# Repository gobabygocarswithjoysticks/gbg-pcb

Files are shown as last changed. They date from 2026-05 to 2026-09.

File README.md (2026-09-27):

# GBG PCB

# A PCB for controlling the motors in a [go baby go car with joystick control](https://gobabygocarswithjoysticks.github.io/index/)

## Questions? Please email our support line at gbg-pcb@googlegroups.com

https://github.com/gobabygocarswithjoysticks/gbg-pcb



V2.3

### This board replaces the control box of a car's original electronics or the separate ESCs and Arduino in the [usual joystick go baby go modification](https://gobabygocarswithjoysticks.github.io/index/). The board has screw terminals for connecting to the battery, motors, and the joystick. With this circuit board, a car can be converted to joystick control without any soldering.

### Voltage input: 6V, 12V, or 24V (absolute maximum 4.6V-35V)

### Controls two motors: one for each wheel so that the car can turn in place.

## V2 vs V1
* V2 GBG-PCBs (V2.3+) can run from 6-24 volt batteries.
* V2.1 and V2.2 GBG-PCBs can run from 6 to 12 volt batteries (maximum of 18 volts). 
* Version 1 GBG-PCBs had a higher, 10+ amp current capacity and a lower part count (easier assembly) but only runs on 12 volts.
* Version 2 boards can be [configured](https://gobabygocarswithjoysticks.github.io/gbg-pcb/instructions/instructions#new-in-v2-weelye-control-box-compatible) with battery, motor, and signal plugs that match the plugs on the common weelye control boxes. This means some cars can be converted to joystick control without cutting any wires. 
* Version 2 boards can supply [8 amps](/testing.md) per motor continuously.
* For the previous versions of the GBG-PCB see https://github.com/gobabygocarswithjoysticks/gbg-pcb/tree/version_1 

# Want one?
Here's a few options:
* Please feel free to use these [files](/PCB_production) and get boards yourself. There are instructions [here](https://gobabygocarswithjoysticks.github.io/gbg-pcb/instructions/how-to-make-boards/how-to-make-boards) for how to make GBG-PCBs by hand. A board costs approximately $40-$100 depending on what quantity it is built in.
* [Use this PCBWay link to order fully assembled boards](https://www.pcbway.com/project/shareproject/GBG_PCB_Go_Baby_Go_Printed_Circuit_Board_V2_2_standard_b412e472.html). Or, alternative PCBWay links if you want to complete the assembly yourself: [PCBWay can do everything but leave the battery, motor, and button connectors off](https://www.pcbway.com/project/shareproject/GBG_PCB_Go_Baby_Go_Printed_Circuit_Board_V2_2_no_motor_battery_or_button_c_74b587c3.html) or, [PCBWay can do the challenging surface mount soldering and leave the through-hole soldering for you](https://www.pcbway.com/project/shareproject/GBG_PCB_Go_Baby_Go_Printed_Circuit_Board_V2_2_SMD_only_f25d1936.html)
* Email gobabygocarswithjoysticks@gmail.com. We may have a spare V1 or V2 GBG-PCBs that I can sell or donate to you.
* Email pnwassistivetech@gmail.com or visit the [PNW Assistive Technology website](https://pnwassistivetechnology.org/plug-and-drive). Thank you to PNWAT for sponsoring V2 GBG-PCB prototyping runs and being a supplier of V1 and V2 GBG-PCBs (called "plug and drive boards" by PNWAT).

# Software
## The website for uploading software to a GBG-PCB and adjusting settings is here: https://gobabygocarswithjoysticks.github.io/programmer/

# Instructions
## [general instructions for using this PCB](https://gobabygocarswithjoysticks.github.io/gbg-pcb/instructions/instructions)
### [instructions for assembling your own GBG-PCBs](https://gobabygocarswithjoysticks.github.io/gbg-pcb/instructions/how-to-make-boards/how-to-make-boards)
## Index of Instructions for modifying specific models of cars using GBG-PCBs
* [Aosom Jeep - old model](https://gobabygocarswithjoysticks.github.io/gbg-pcb/instructions/car-specific/aosom-038-jeep/instructions)
* [Zupapa Bumper Car](https://gobabygocarswithjoysticks.github.io/gbg-pcb/instructions/car-specific/zupapa-bumper-car/instructions)
* [Flybar Bumper Car](https://gobabygocarswithjoysticks.github.io/gbg-pcb/instructions/car-specific/flybar-bumper-car/instructions)

# Wiring Diagram
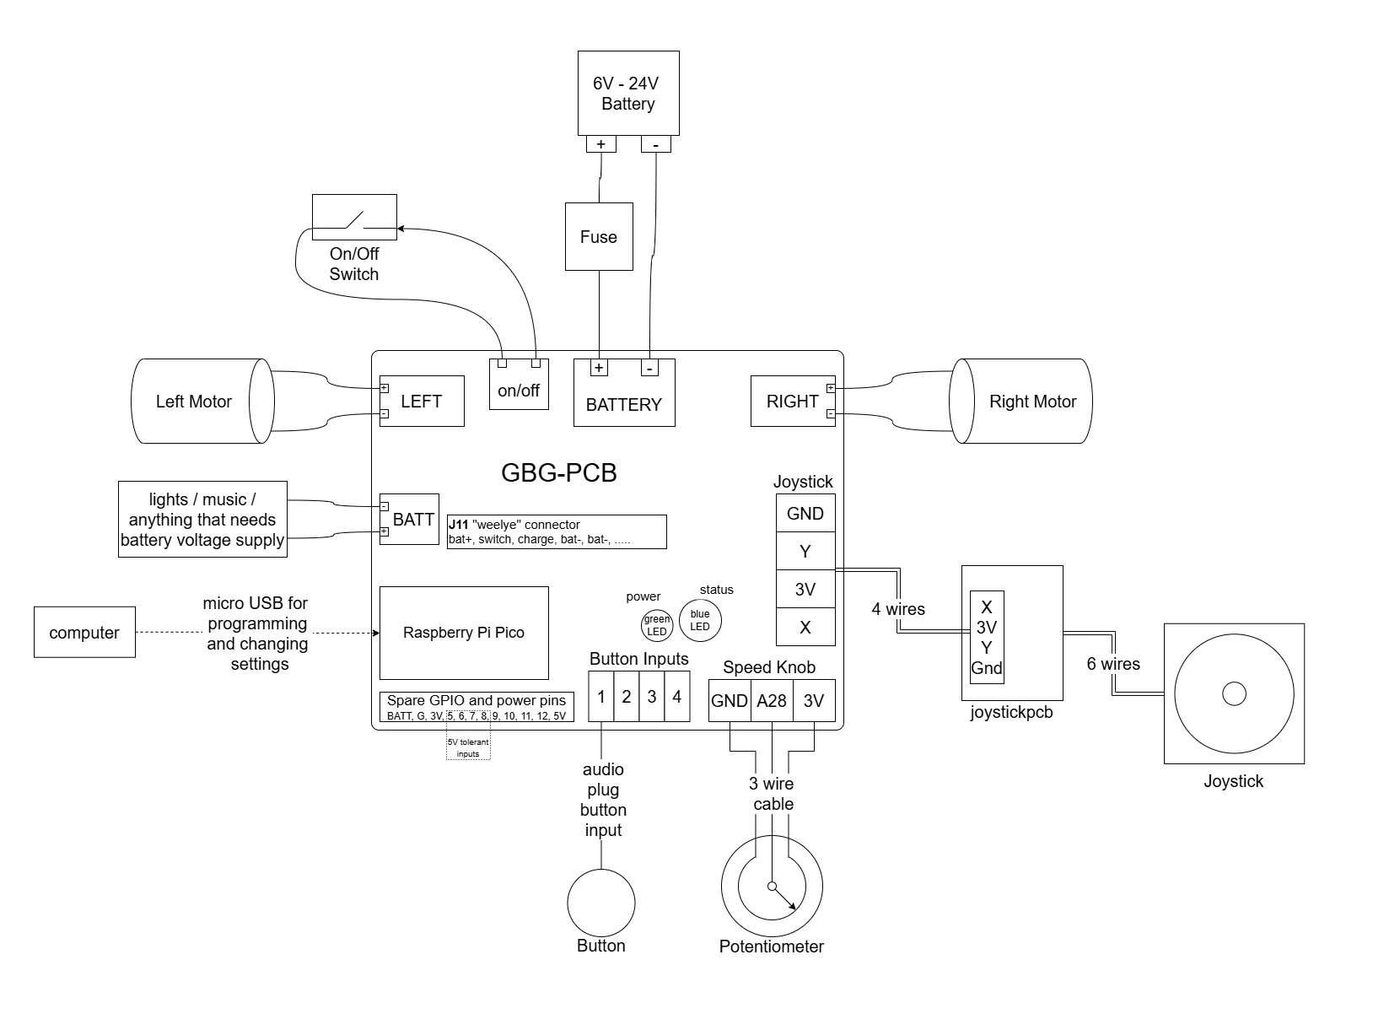
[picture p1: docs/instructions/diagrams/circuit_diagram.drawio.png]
wiring diagram


# [Schematic of PCB](/schematic.pdf)

# [PCB Production files](/PCB_production)

# [joystick to 4 wire cable connector PCB](https://github.com/gobabygocarswithjoysticks/gbg-pcb/tree/main/joystickpcb)
### This keeps you from needing to solder the joystick wires to a 4 wire cable.

# [3D printed case for the GBG-PCB](/case)
See the above link for notes on how to add cooling fans to the case to increase the current capacity.
With fans running, a V2 GBG-PCB has been tested to supply [11 amps](/testing.md).

# notes for people working on the KiCAD for this project
Use KiCAD 10.0

Run [this github action](https://github.com/gobabygocarswithjoysticks/gbg-pcb/actions/workflows/process-kicad.yml) when you push changes to the KiCAD files. The action updates the images of the CAD, the gerber files, the schematic, and other PCB production files. 

# photos
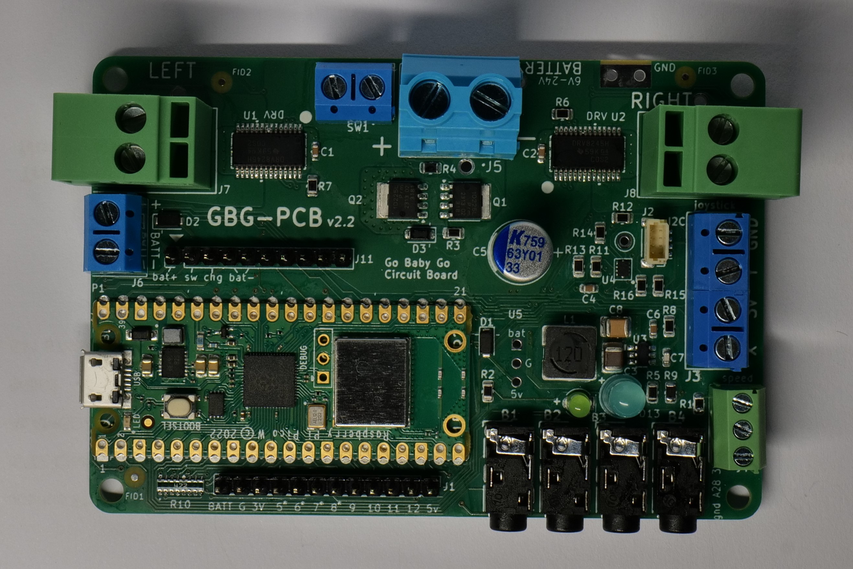
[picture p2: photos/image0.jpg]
view of assembled PCB from the top

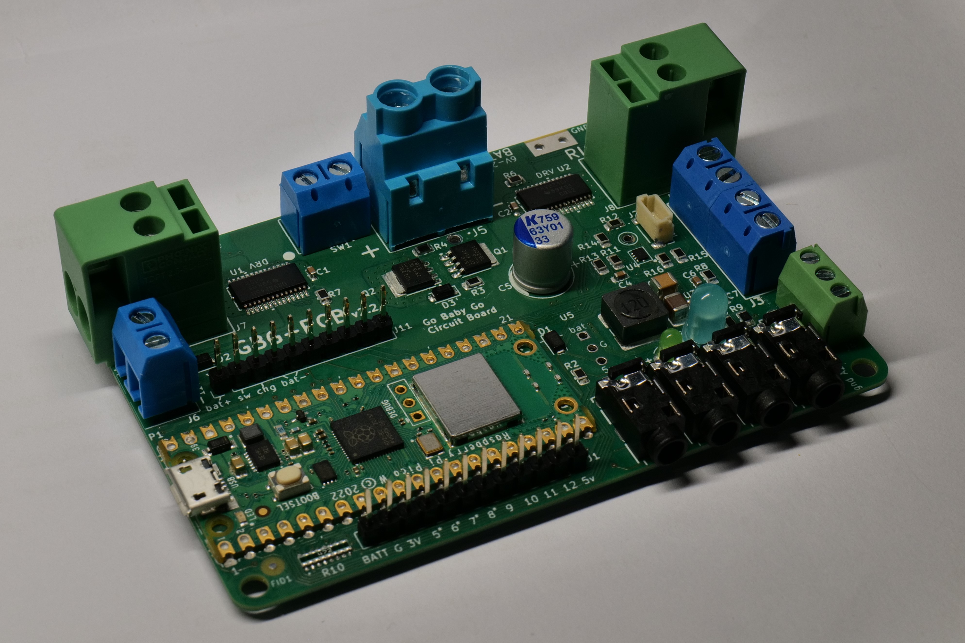
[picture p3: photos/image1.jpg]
view of assembled PCB


# images of CAD

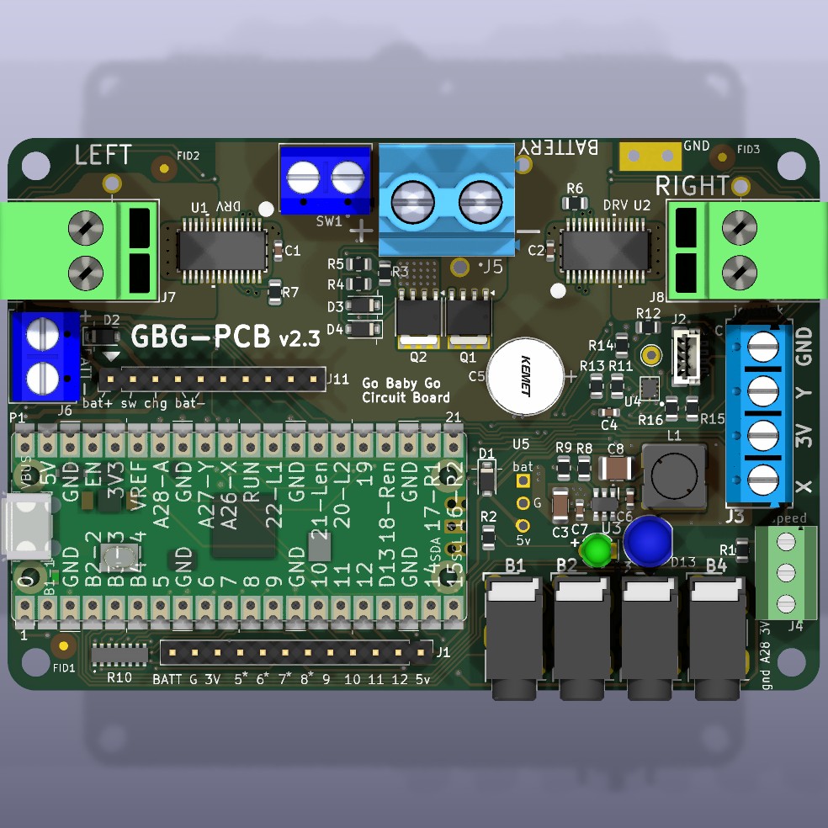
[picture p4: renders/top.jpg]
auto generated image, top view

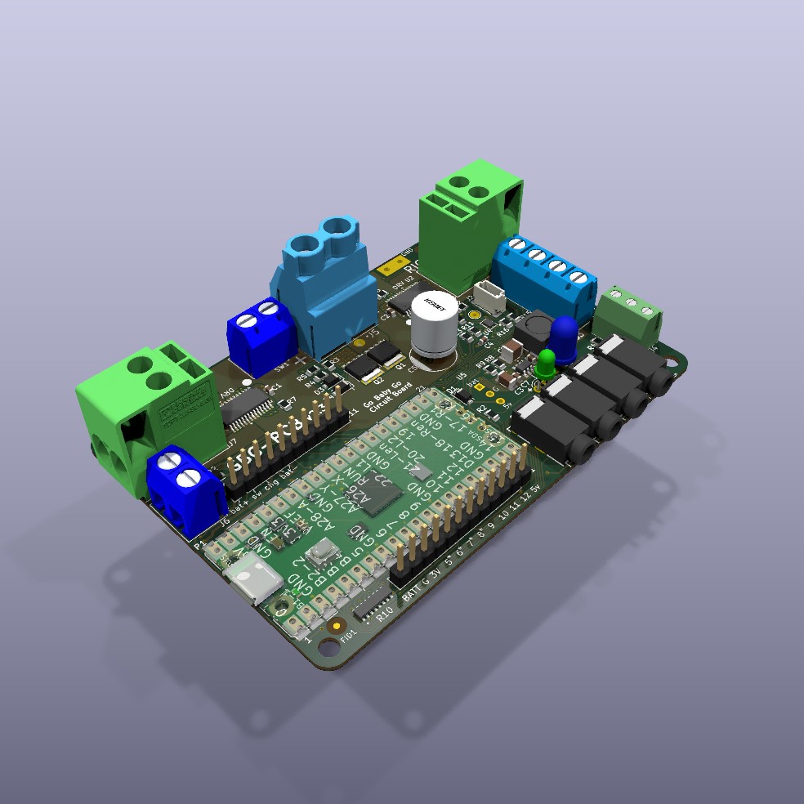
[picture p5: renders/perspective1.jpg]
auto generated image, p1

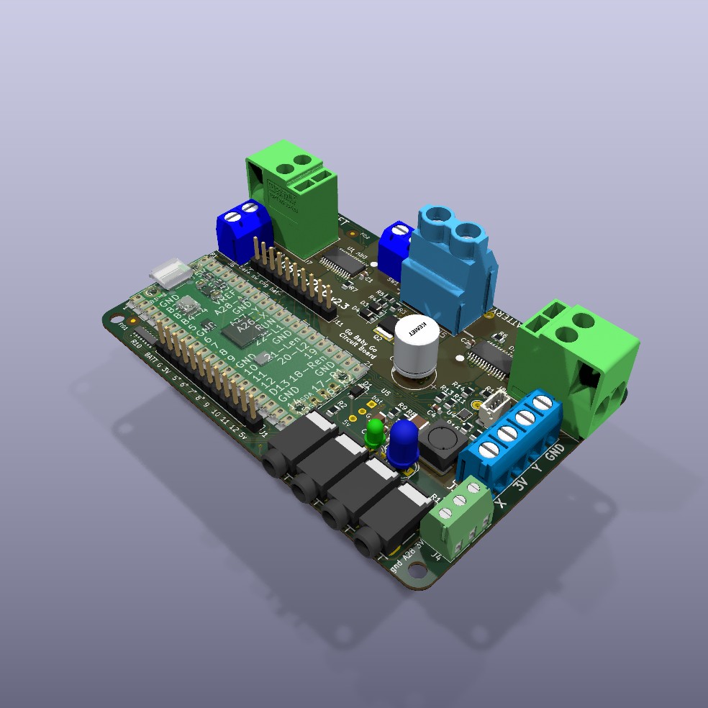
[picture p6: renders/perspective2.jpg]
auto generated image, p2

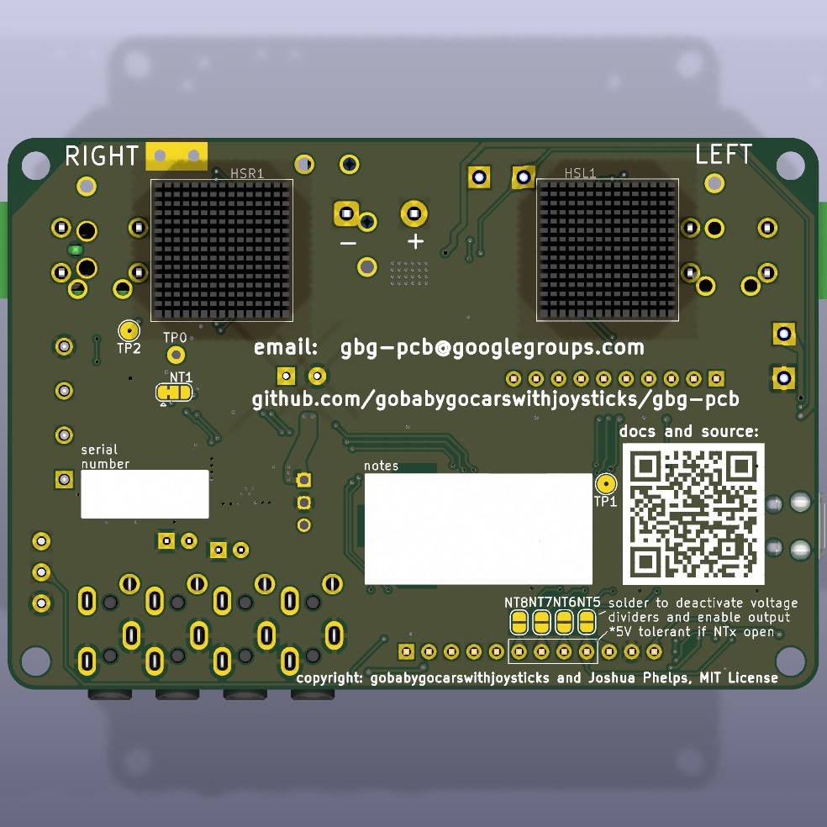
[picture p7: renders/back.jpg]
auto_generated_image, back


# credits

## This project was inspired by the [Go Baby Go project](https://health.oregonstate.edu/gobabygo) that modifies powered ride-on cars for kids with disabilities

## Sponsored by [Pacific North West Assistive Technology](https://pnwassistivetechnology.org/)

PNWAT Logo 3 1 Main CMYK

## Copyright: [gobabygocarswithjoysticks](https://github.com/gobabygocarswithjoysticks/index) and Joshua Phelps, MIT License

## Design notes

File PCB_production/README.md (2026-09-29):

## instructions for how to make GBG-PCBs by hand are [here](https://gobabygocarswithjoysticks.github.io/gbg-pcb/instructions/how-to-make-boards/how-to-make-boards)

## send [gerbers.zip](/PCB_production/gerbers.zip) to a PCB fabrication company

### [F_SolderPasteMask.dxf](/PCB_production/F_SolderPasteMask.dxf) might help you get a solder stencil (but most suppliers prefer to receive the gerber files when ordering a solder stencil).

## The [position.csv](/PCB_production/position.csv) file has the locations for the surface mount components

## Bill Of Materials (BOM)
### please email gbg-pcb@googlegroups.com if components are out of stock and you need recommendations for alternatives

[BOM.csv](/PCB_production/BOM.csv) is the normal list of parts (using screw terminals for connections).

[BOM-with-DNP.csv](/PCB_production/BOM-with-DNP.csv) includes alternative parts that you could choose some of, for other configurations of the board.

[BOM-without-motor-battery-button-speed-connectors.csv](/PCB_production/BOM-without-motor-battery-button-speed-connectors.csv) is a list of parts without the motor, battery, and button connectors that can be used to get assembled boards that can be customized with either screw terminals or weelye-style tabs by doing just a little bit of through-hole soldering.

[BOM-only-smd.csv](/PCB_production/BOM-only-smd.csv) is a list of the surface mount parts that can be used to order boards with surface mount components soldered for you but all of the easier-to-solder through-hole components are left for you to buy and solder.

Here is the V2.3 BOM.csv uploaded to a [Digikey list](https://www.digikey.com/en/mylists/list/KOKUQVA6NC)

## [joystick to 4 wire cable connector PCB](https://github.com/gobabygocarswithjoysticks/gbg-pcb/tree/main/joystickpcb)
This keeps you from needing to solder the joystick wires to a 4 wire cable.

## [interactive BOM to help with assembly](https://gobabygocarswithjoysticks.github.io/gbg-pcb/ibom/ibom.html)

## parameters for PCBs:
* 1oz copper
* 1.0mm board thickness
* 5mil/5mil
* 0.25mm holes
* solder stencils should be 0.12mm
* solder stencils should be "non-framework"
* I suggest lead-free HASL, but match your solder type

## other configurations

### alternate voltage regulator (U5)
Replace U3, C3, C6, C7, C8, R8, R9, L1

Choose a single THT module that outputs 5V. Make sure the pinout matches. Make sure the min and max input voltage are compatible with your battery. It's ok if the output voltage sags below 5 volts as the input approaches 5 volts but make sure the regulator you choose doesn't start blinking on and off as the input approaches 5 volts, if you plan to use cars with 6 volt batteries.

Consider pololu5593, D78B05T, RBT05W24S05

### alternate battery and motor connectors (Weelye mode)
The GBG-PCB includes pads for adding connectors that match the connectors on some common weelye control boxes like the RX22 and RX7.

* J102 and J103 replace J5 (battery)
* J100 and J101 replace J7 (left)
* J104 OR J105 replaces J8 (choose the plug that matches your control box)

J104:

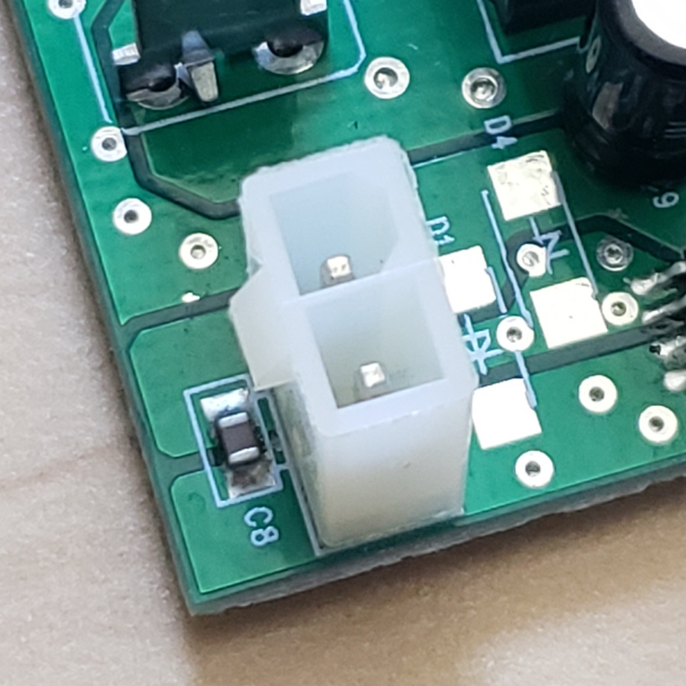
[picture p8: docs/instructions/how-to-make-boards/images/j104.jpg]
two-pin shrouded connector 23-2159151002-ND


J105:

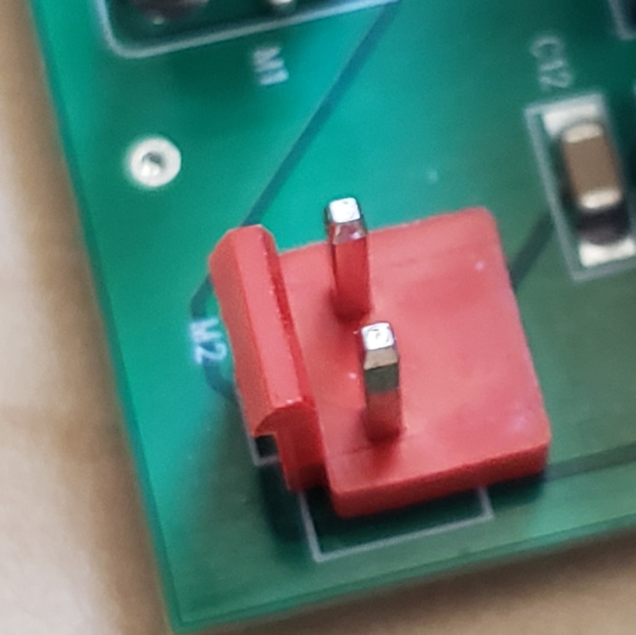
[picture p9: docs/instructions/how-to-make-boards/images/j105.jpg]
two-pin connector A111830-ND


### other models of Raspberry Pi Pico (P1)
If you want to be able to change settings and remote override the car over a wifi connection [(see information here)](https://github.com/gobabygocarswithjoysticks/car-code/tree/main/rcdocs#notes-on-wifiwebsite-remote-control) choose a Pico 1W or Pico 2W.

### cost saving by removing optional features

#### button ports
If you know that you will only use joystick input and won't use button input you can omit 

B1, B2, B3, B4

#### i2c connector
If you don't plan to connect I2C devices (most likely you don't need this) you can omit

J2

#### battery and current monitor
If you don't need the PCB to be able to detect low battery voltage or how much current the motors are drawing you can omit the following parts:

U4, R11, R12, R13, R14, R20, C4

#### speed knob
If you know that you will not install a speed adjustment knob you can omit 

J4

#### [consider an alternate voltage regulator](https://github.com/gobabygocarswithjoysticks/gbg-pcb/blob/main/PCB_production/README.md#alternate-voltage-regulator-u5)

Using a THT module might not be significantly cheaper but it could save you time during assembly.

## questions for suppliers to ask
* pico1 or pico1W?
* include button jacks?
* include chip that monitors voltage and current?
* screw terminals or "weelye mode"?
    * if weelye mode, the standard headers for J11 could be changed to match the specific boards you're using

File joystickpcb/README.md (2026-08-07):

solderless way to connect the joystick to the 4 wire cable

## [gerber files](https://github.com/gobabygocarswithjoysticks/gbg-pcb/raw/main/joystickpcb/gerbers-joystickpcb-v1.0.zip) (ideally 0.8mm thick)

You can send the gerber files to a PCB manufacturer of your choice, or use this [OSHPARK link](https://oshpark.com/shared_projects/SELEKcav) or this [PCBWAY link](https://www.pcbway.com/project/shareproject/joystickpcb_v1_0_d95f5fa0.html) to order this PCB.

## Components
| name                  | description  | manufacturer      | part number | digikey link                                                                       |
|-----------------------|--------------|-------------------|-------------|------------------------------------------------------------------------------------|
| 6 pin plug            | 6 pin JST PH | JST Sales America | B6B-PH-K-S  | https://www.digikey.com/en/products/detail/jst-sales-america-inc/B6B-PH-K-S/926615 |
| 4 wire screw terminal | 4 wire 3.5mm | Phoenix Contact OR On Shore Technology Inc.  | 1984633 OR OSTTE040104 | https://www.digikey.com/en/products/detail/phoenix-contact/1984633/768668  OR https://www.digikey.com/en/products/detail/on-shore-technology-inc/OSTTE040104/2351818       |

3d

pcb

joystick
The wires between the joystickpcb and the GBG-PCB would be a longer 4 wire cable when installed in a car.

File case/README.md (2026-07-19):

To protect your GBG-PCB, print the top and bottom parts. 

Assemble using 4 12mm M3 bolts and 4 M3 nuts.

To add fans (fans can be used to cool the boards and increase the maximum current that the boards can supply), add the following parts:
* Print the fan-funnel part and the fan-cover part
* Get 2 cooling fans (choose voltage compatible with your car)
    * [5V, 3.5-6](https://www.digikey.com/en/products/detail/sunon-fans/MF40200V1-1000U-A99/6198712), or 
    * [12V, 4.5-13.8](https://www.digikey.com/en/products/detail/sunon-fans/MF40201V1-1000U-A99/6198971), or 
    * [24V 8-27.6](https://www.digikey.com/en/products/detail/sunon-fans/MF40202V1-1000U-A99/6198716)
* Assemble using 4 40mm M4 bolts and 4 M4 nuts
    * Bolt the fans to the bottom piece of the case before assembling the top and bottom parts around the GBG-PCB.

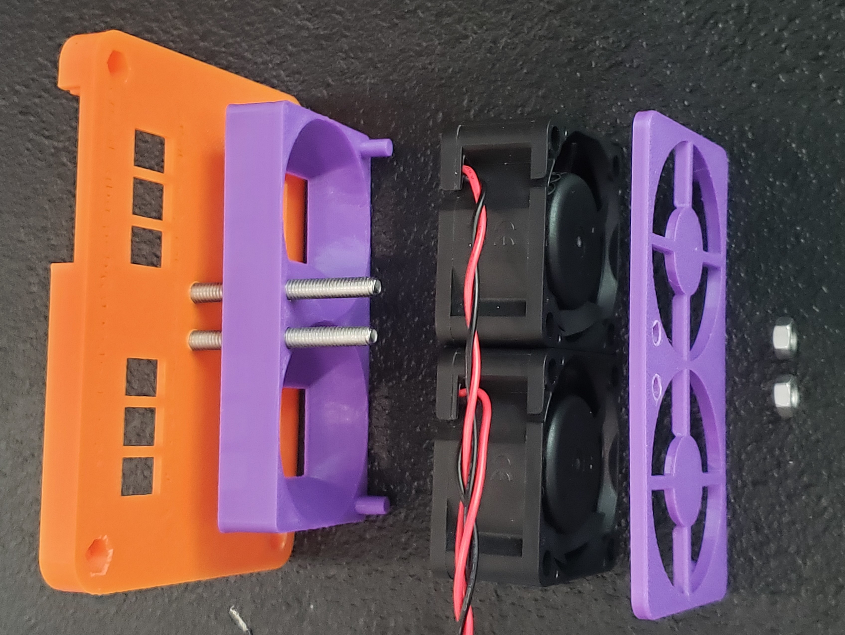
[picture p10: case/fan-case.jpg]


case.FCStd is a FreeCAD file

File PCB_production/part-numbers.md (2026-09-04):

# GBG-PCB Part Numbers

## GBG-PCB-V2.1
## GBG-PCB-V2.2

### Examples
GBG-PCB-V2.1-A1-B1-C1-D1-E1-F1-G1-H1-J1-K0-L1-M1-N1-P1-Q1

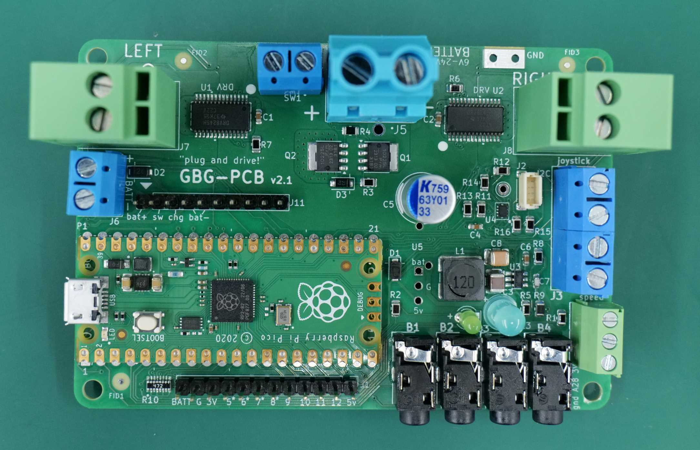
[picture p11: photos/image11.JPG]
v2.1a


GBG-PCB-V2.1-A2-B2-C0-D1-E1-F1-G1-H1-J1-K0-L1-M1-N1-P1-Q1

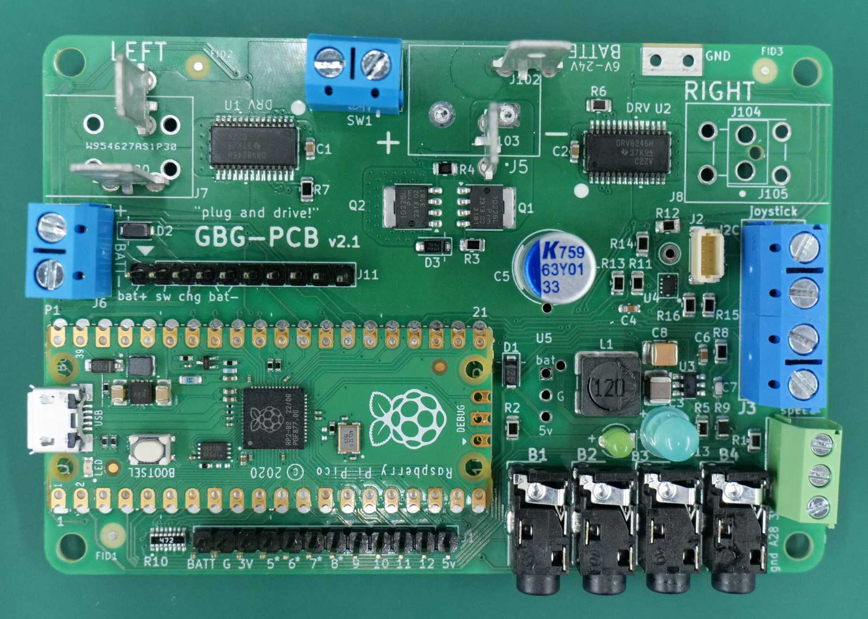
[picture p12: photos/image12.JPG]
v2.1b


### A: battery connector
#### 0: not installed
#### 1: screw terminal (J5)
#### 2: tabs for Weelye mode (J102 J103)

### B: left motor connector
#### 0: not installed
#### 1: screw terminal (J7)
#### 2: tabs for Weelye mode (J100 J101)

### C: right motor connector
#### 0: not installed
#### 1: screw terminal
#### 2: Molex 2159151002 (J104)
#### 3: TE 1-1123723-2 (J105)
#### 4: tabs for Weelye mode (J106 J107), V2.2 only

### D: pico
#### 0: not installed
#### 1: Pico 1
#### 2: Pico 2
#### 1W: Pico 1W (wifi)
#### 2W: Pico 2W (wifi)

### E: voltage regulator
#### 0: not installed
#### 1: default (U3, C3, R5, C6, L1, C7, R8, R9, C8)

### F: button ports
#### 0: not installed
#### 1: soldered (B1, B2, B3, B4)

### G: I2C connector
#### 0: not installed
#### 1: soldered (J2)

### H: battery and current monitor
#### 0: not installed
#### 1: soldered (U4, R11, R12, R13, R14, R20, C4)

### J: speed knob
#### 0: not installed
#### 1: soldered (J4)

### K: case
#### 0: no case
#### 1: default case
#### 2: case with 12V fans 

### L: resistor divider for 5V tolerant pins on 5,6,7,8
#### 0: not installed
#### 1: installed (R10)
#### 2: output enabled

### M:  extra GPIO pins
#### 0: not installed
#### 1: installed (J1)

### N: power switch and charging pins ("J11 weelye connector")
#### 0: not installed
#### 1: installed (J11)

### P: switch terminal
#### 0: not installed
#### 1: installed (SW1)

### Q: power terminal
#### 0: not installed
#### 1: installed (J6)

## GBG-PCB-V1.1
## GBG-PCB-V1.2

### Examples

GBG-PCB-V1.2-D1W-F1-J1-K0-M1-P1-Q1

v1.2

### V: version
#### 1.1 - uses a single long heatsink
#### 1.2 - uses two heatsinks, one for each motor driver

### D: pico
#### 0: not installed
#### 1: Pico 1
#### 2: Pico 2
#### 1W: Pico 1W (wifi)
#### 2W: Pico 2W (wifi)

### F: button ports
#### 0: not installed
#### 1: soldered (B1, B2, B3, B4)

### J: speed knob
#### 0: not installed
#### 1: soldered (J4)

### K: case
#### 0: no case

### M:  extra GPIO pins
#### 0: not installed
#### 1: installed (J1)

### P: switch terminal
#### 0: not installed
#### 1: installed (SW1)

### Q: power terminal
#### 0: not installed
#### 1: installed (J12)

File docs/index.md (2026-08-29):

[back to GitHub](https://github.com/gobabygocarswithjoysticks/gbg-pcb)

# A PCB for controlling the motors in a [go baby go car with joystick control](https://gobabygocarswithjoysticks.github.io/index/)
This circuit board replaces the separate ESCs and Arduino with screw terminals for the connections to the motors and battery so you won't need to solder anything.

# instructions for using this PCB to modify a car
## [general instructions for using this PCB](https://gobabygocarswithjoysticks.github.io/gbg-pcb/instructions/instructions)
## [instructions for making your own GBG-PCBs](https://gobabygocarswithjoysticks.github.io/gbg-pcb/instructions/how-to-make-boards/how-to-make-boards)
### [instructions specifically for the Aosom Jeep](https://gobabygocarswithjoysticks.github.io/gbg-pcb/instructions/car-specific/aosom-038-jeep/instructions)
### [instructions specifically for the Zupapa bumper car](https://gobabygocarswithjoysticks.github.io/gbg-pcb/instructions/car-specific/zupapa-bumper-car/instructions)
### [instructions specifically for the Flybar bumper car](https://gobabygocarswithjoysticks.github.io/gbg-pcb/instructions/car-specific/flybar-bumper-car/instructions)

## source files
[https://github.com/gobabygocarswithjoysticks/gbg-pcb](https://github.com/gobabygocarswithjoysticks/gbg-pcb)

## images

pcb top view 3d render

pcb photo

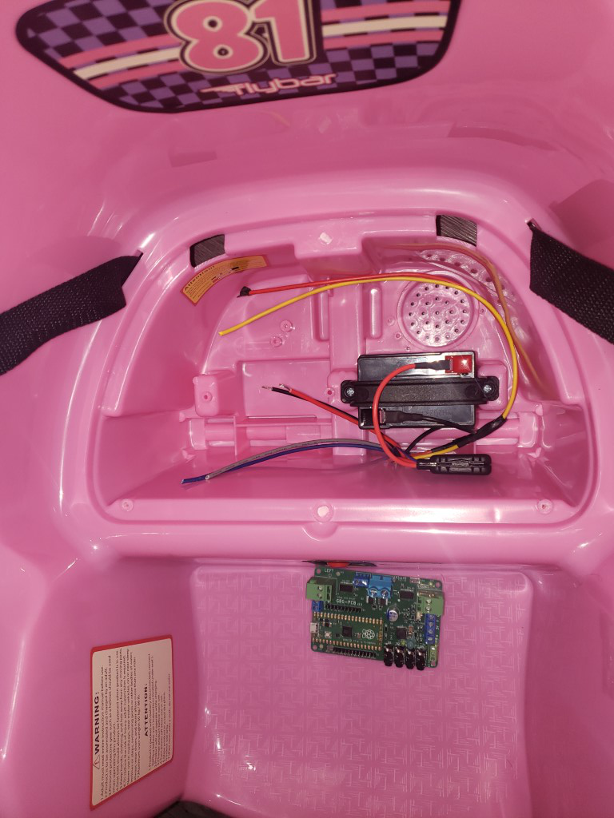
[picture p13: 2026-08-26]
docs/instructions/car-specific/flybar-bumper-car/photos/wires-in-seat.jpg

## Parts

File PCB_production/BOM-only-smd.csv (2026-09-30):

Reference | Value | Footprint | Manufacturer_Name | Manufacturer_Part_Number | digikey_part_number | mount_type | QUANTITY
C1,C2,C4 | 0.1uF | Capacitor_SMD:C_0603_1608Metric | TDK Corporation | CGA3E2X7R1H104M080AA | 445-12561-1-ND | smd | 3
C3 | 1uF | Capacitor_SMD:C_1206_3216Metric | TDK | C3216X7R1H105K160AB | 445-1423-1-ND | smd | 1
C6 | 0.1uF | Capacitor_SMD:C_0603_1608Metric | TDK | CGA3E2X7R1E104K080AA | 445-5667-1-ND | smd | 1
C7 | 0.1uF | Capacitor_SMD:C_0603_1608Metric | Murata Electronics | GRM188R72A104KA35D | 490-3285-1-ND | smd | 1
C8 | 22uF | Capacitor_SMD:C_1210_3225Metric | Taiyo Yuden | MSASE32MSB7226KPNB25 | 587-MSASE32MSB7226KPNB25CT-ND | smd | 1
D1,D2 | D_Schottky | Diode_SMD:D_SOD-123F | Good-Ark Semiconductor | FS26 | 4786-FS26CT-ND | smd | 2
D3,D4 | 18V zener | Diode_SMD:D_SOD-123F | Vishay General Semiconductor - Diodes Division | MMSZ5248B-E3-18 | MMSZ5248B-E3-18GICT-ND | smd | 2
J2 | Conn_01x04 | Connector_JST:JST_SH_BM04B-SRSS-TB_1x04-1MP_P1.00mm_Vertical | JST Sales America Inc. | BM04B-SRSS-TB | 455-BM04B-SRSS-TBCT-ND | smd | 1
L1 | 10uH | kicad libraries:IND_SRR6038 | Bourns | SRR6038-100Y | SRR6038-100YCT-ND | smd | 1
P1 | rpi pico 1 W | Module:RaspberryPi_Pico_Common_SMD | Raspberry Pi | SC0918 | 2648-SC0918CT-ND | smd | 1
Q1,Q2 | PSMN1R0-40YLDX | Package_TO_SOT_SMD:LFPAK56 | Nexperia USA Inc. | PSMN1R0-40YLDX | 1727-1856-1-ND | smd | 2
R1,R2 | 220 | Resistor_SMD:R_0805_2012Metric | Vishay Dale | CRCW0805220RJNEA | 541-220ACT-ND | smd | 2
R3,R15,R16 | 3.3k | Resistor_SMD:R_0805_2012Metric | Vishay Dale | CRCW08053K30FKEA | 541-3.30KCCT-ND | smd | 3
R4,R5,R9 | 22.1k | Resistor_SMD:R_0805_2012Metric | Vishay Dale | CRCW080522K1FKEA | 541-22.1KCCT-ND | smd | 3
R6,R7,R14 | 8.2k | Resistor_SMD:R_0805_2012Metric | Vishay Dale | CRCW08058K20JNEA | 541-8.2KACT-ND | smd | 3
R8 | 115k | Resistor_SMD:R_0805_2012Metric | Vishay Dale | CRCW0805115KFKEA | 541-115KCCT-ND | smd | 1
R10 | 4.7k | kicad libraries:742C163472JP | CTS Resistor Products | 742C163472JP | 60-742C163472JPCT-ND | smd | 1
R11,R12 | 604 | Resistor_SMD:R_0805_2012Metric | Vishay Dale | CRCW0805604RFKEA | 541-604CCT-ND | smd | 2
R13 | 100k | Resistor_SMD:R_0805_2012Metric | Vishay Dale | CRCW0805100KFKEA | 541-100KCCT-ND | smd | 1
U1,U2 | DRV8245HQPWPRQ1 | kicad libraries:HTSSOP28_PWP_TEX | Texas Instruments | DRV8245HQPWPRQ1 | 296-DRV8245HQPWPRQ1CT-ND | smd | 2
U3 | LMR54410DBVR | kicad libraries:SOT95P280X145-6N | Texas Instruments | LMR54410DBVR | 296-LMR54410DBVRCT-ND | smd | 1
U4 | TLA2024IRUGR | kicad libraries:IC_TLA2024IRUGR | Texas Instruments | TLA2024IRUGR | 296-51661-1-ND | smd | 1

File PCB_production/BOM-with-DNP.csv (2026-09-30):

Reference | Value | Footprint | Manufacturer_Name | Manufacturer_Part_Number | digikey_part_number | mount_type | QUANTITY
3V1 | green | LED_THT:LED_D3.0mm | American Bright Optoelectronics Corporation | BL-B2141K | 2007-BL-B2141K-ND | tht | 1
B1-B4 | ASJ-200-B-HT | kicad libraries:ASJ200BHT | Adam Tech | ASJ-200-B-HT | 2057-ASJ-200-B-HT-ND | tht | 4
C1,C2,C4 | 0.1uF | Capacitor_SMD:C_0603_1608Metric | TDK Corporation | CGA3E2X7R1H104M080AA | 445-12561-1-ND | smd | 3
C3 | 1uF | Capacitor_SMD:C_1206_3216Metric | TDK | C3216X7R1H105K160AB | 445-1423-1-ND | smd | 1
C5 | 33uf | kicad libraries:CAP_KK-8x8_KEM | KEMET | A759KK336M1JAAE036 | 399-A759KK336M1JAAE036-ND | tht | 1
C6 | 0.1uF | Capacitor_SMD:C_0603_1608Metric | TDK | CGA3E2X7R1E104K080AA | 445-5667-1-ND | smd | 1
C7 | 0.1uF | Capacitor_SMD:C_0603_1608Metric | Murata Electronics | GRM188R72A104KA35D | 490-3285-1-ND | smd | 1
C8 | 22uF | Capacitor_SMD:C_1210_3225Metric | Taiyo Yuden | MSASE32MSB7226KPNB25 | 587-MSASE32MSB7226KPNB25CT-ND | smd | 1
D1,D2 | D_Schottky | Diode_SMD:D_SOD-123F | Good-Ark Semiconductor | FS26 | 4786-FS26CT-ND | smd | 2
D3,D4 | 18V zener | Diode_SMD:D_SOD-123F | Vishay General Semiconductor - Diodes Division | MMSZ5248B-E3-18 | MMSZ5248B-E3-18GICT-ND | smd | 2
D13 | blue | LED_THT:LED_D5.0mm | American Bright Optoelectronics Corporation | BL-BBX1V4V-2-B02 | 2007-BL-BBX1V4V-2-B02-ND | tht | 1
HSL1,HSR1 | Heatsink | kicad libraries:heatsink 375424B00034G | Boyd Laconia, LLC | 375424B00034G | 375424B00034G-ND | tht | 2
J1 | 12 2.54mm pitch header pins | Connector_PinHeader_2.54mm:PinHeader_1x12_P2.54mm_Vertical | Any Manufacturer | PH1-12-UA | 2057-PH1-12-UA-ND | tht | 1
J2 | Conn_01x04 | Connector_JST:JST_SH_BM04B-SRSS-TB_1x04-1MP_P1.00mm_Vertical | JST Sales America Inc. | BM04B-SRSS-TB | 455-BM04B-SRSS-TBCT-ND | smd | 1
J3 | joystick | kicad libraries:TC0403620000G | Amphenol Anytek | TC0403620000G | TC0403620000G-ND | tht | 1
J4 | speed knob | kicad libraries:SAMESKY_TB0011-350-03GR | Same Sky (Formerly CUI Devices) | TB0011-350-03GR | 2223-TB0011-350-03GR-ND | tht | 1
J5 | TB005-762-02BE | kicad libraries:CUI_TB005-762-02BE | Same Sky (Formerly CUI Devices) | TB005-762-02BE | 102-6189-ND | tht | 1
J6,SW1 | screw terminal | kicad libraries:EBBA-02-C-SS-BU | Adam Tech | EBBA-02-C-SS-BU | 2057-EBBA-02-C-SS-BU-ND | tht | 2
J7,J8 | 1017491 | kicad libraries:CONN_1017491 | Phoenix Contact | 1017491 | 277-17493-ND | tht | 2
J11 | Conn_01x10_Pin | Connector_PinHeader_2.54mm:PinHeader_1x10_P2.54mm_Vertical | Any Manufacturer | PH1-10-UA | 2057-PH1-10-UA-ND | tht | 1
J100-J103,J106,J107 | 0197054001 | kicad libraries:0197054001 | Molex | 0197054001 | WM2982-ND | tht | 6
J104 | wellye style | kicad libraries:CONN02_2159151002_MOL | Molex | 2159151002 | 23-2159151002-ND | tht | 1
J105 | wellye style | kicad libraries:TE_1-1123723-2 | TE Connectivity AMP Connectors | 1-1123723-2 | A111830-ND | tht | 1
L1 | 10uH | kicad libraries:IND_SRR6038 | Bourns | SRR6038-100Y | SRR6038-100YCT-ND | smd | 1
M1,M2 | [5V, 3.5-6] MF40200V1-1000U-A99, or [12V, 4.5-13.8] MF40201V1-1000U-A99, or [24V 8-27.6] MF40202V1-1000U-A99 |  | Sunon Fans | [5V, 3.5-6] MF40200V1-1000U-A99, or [12V, 4.5-13.8] MF40201V1-1000U-A99, or [24V 8-27.6] MF40202V1-1000U-A99 | [5V, 3.5-6] MF40200V1-1000U-A99, or [12V, 4.5-13.8] MF40201V1-1000U-A99, or [24V 8-27.6] MF40202V1-1000U-A99 | tht | 2
P1 | rpi pico 1 W | Module:RaspberryPi_Pico_Common_SMD | Raspberry Pi | SC0918 | 2648-SC0918CT-ND | smd | 1
Q1,Q2 | PSMN1R0-40YLDX | Package_TO_SOT_SMD:LFPAK56 | Nexperia USA Inc. | PSMN1R0-40YLDX | 1727-1856-1-ND | smd | 2
R1,R2 | 220 | Resistor_SMD:R_0805_2012Metric | Vishay Dale | CRCW0805220RJNEA | 541-220ACT-ND | smd | 2
R3,R15,R16 | 3.3k | Resistor_SMD:R_0805_2012Metric | Vishay Dale | CRCW08053K30FKEA | 541-3.30KCCT-ND | smd | 3
R4,R5,R9 | 22.1k | Resistor_SMD:R_0805_2012Metric | Vishay Dale | CRCW080522K1FKEA | 541-22.1KCCT-ND | smd | 3
R6,R7,R14 | 8.2k | Resistor_SMD:R_0805_2012Metric | Vishay Dale | CRCW08058K20JNEA | 541-8.2KACT-ND | smd | 3
R8 | 115k | Resistor_SMD:R_0805_2012Metric | Vishay Dale | CRCW0805115KFKEA | 541-115KCCT-ND | smd | 1
R10 | 4.7k | kicad libraries:742C163472JP | CTS Resistor Products | 742C163472JP | 60-742C163472JPCT-ND | smd | 1
R11,R12 | 604 | Resistor_SMD:R_0805_2012Metric | Vishay Dale | CRCW0805604RFKEA | 541-604CCT-ND | smd | 2
R13 | 100k | Resistor_SMD:R_0805_2012Metric | Vishay Dale | CRCW0805100KFKEA | 541-100KCCT-ND | smd | 1
U1,U2 | DRV8245HQPWPRQ1 | kicad libraries:HTSSOP28_PWP_TEX | Texas Instruments | DRV8245HQPWPRQ1 | 296-DRV8245HQPWPRQ1CT-ND | smd | 2
U3 | LMR54410DBVR | kicad libraries:SOT95P280X145-6N | Texas Instruments | LMR54410DBVR | 296-LMR54410DBVRCT-ND | smd | 1
U4 | TLA2024IRUGR | kicad libraries:IC_TLA2024IRUGR | Texas Instruments | TLA2024IRUGR | 296-51661-1-ND | smd | 1

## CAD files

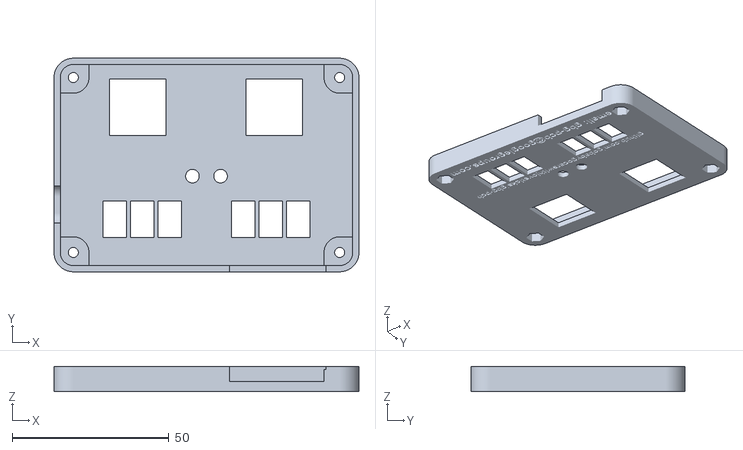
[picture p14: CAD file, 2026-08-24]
case/gbg-pcb-case-bottom.stl
97.4 x 68.2 x 8.00

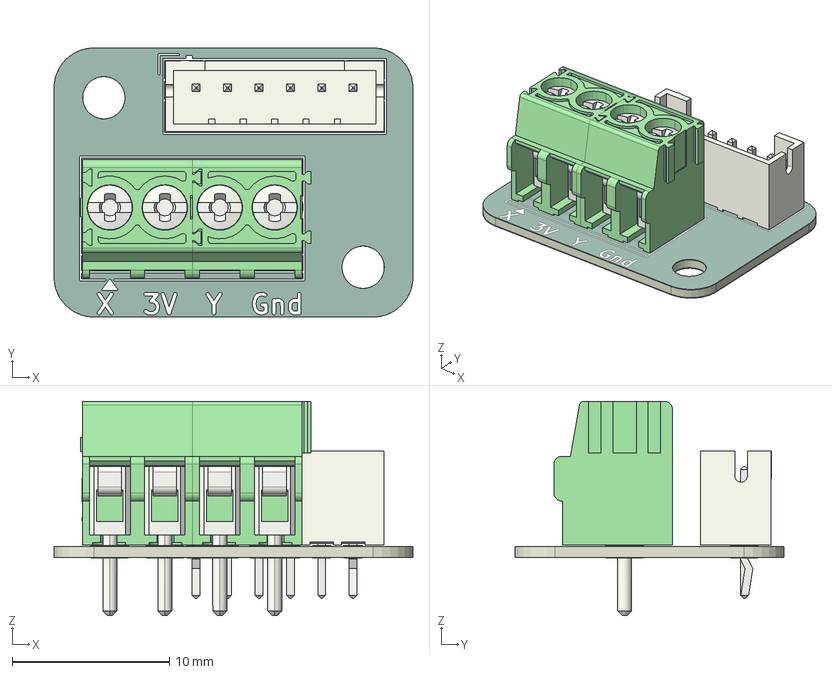
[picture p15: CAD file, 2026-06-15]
joystickpcb/images/joystickpcb.step
22.9 x 17.1 x 13.7 mm
JST_PH_B6B-PH-K_1x06_P2.00mm_Vertical
joystickpcb_pad
joystickpcb_silkscreen x 2
joystickpcb_soldermask x 2
joystickpcb_PCB

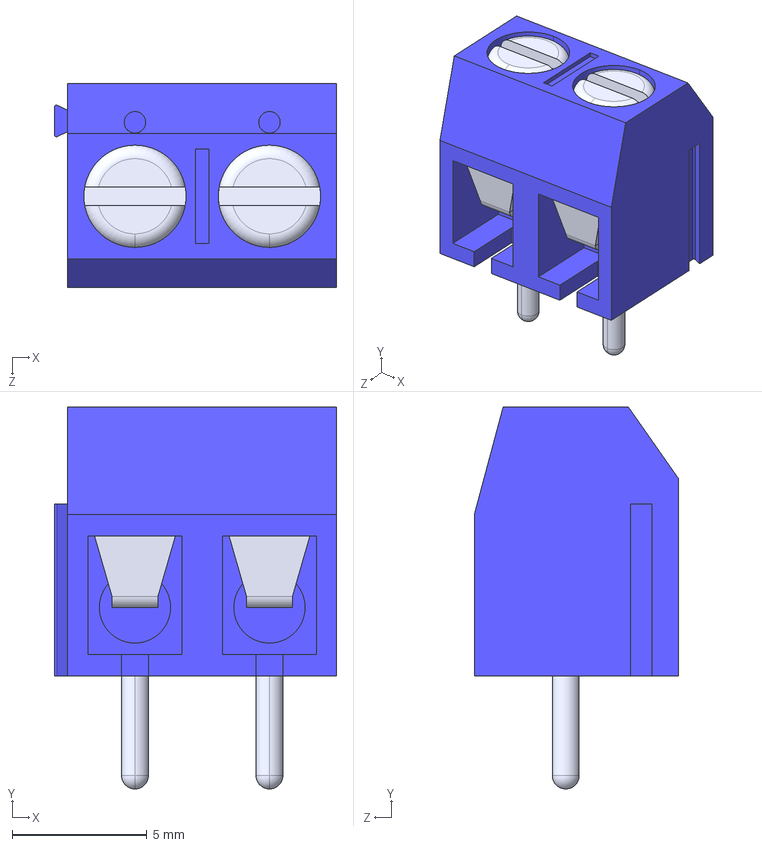
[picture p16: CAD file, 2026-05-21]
kicad/kicad libraries/EBBA-02-C-SS-BU--3DModel-STEP-510211.STEP
10.5 x 14.2 x 7.60 mm

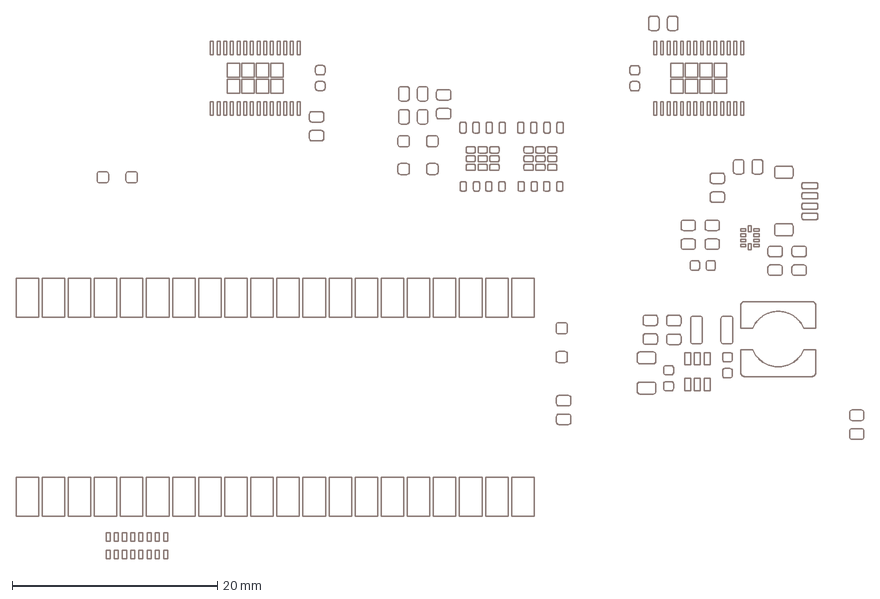
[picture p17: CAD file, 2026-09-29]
PCB_production/F_SolderPasteMask.dxf
82.6 x 52.8 mm

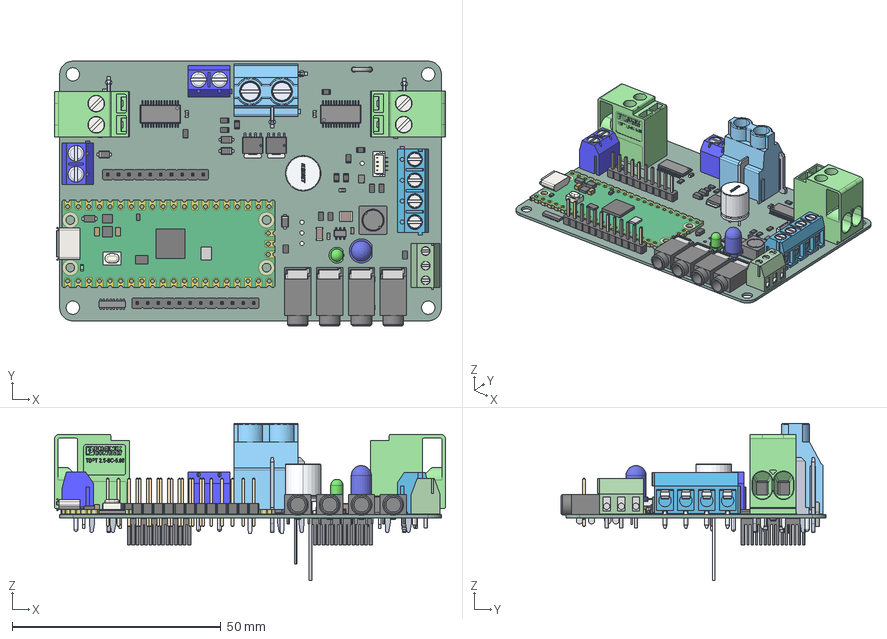
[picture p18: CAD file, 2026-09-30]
renders/gbg-pcb.step
93.6 x 63.4 x 37.7 mm
Pins
ADS1115IRUGR
BODY-SOT
LEAD-SOT x 6
ASJ-200-B-HT x 4
EBBA-02-C-SS-BU x 2
SRR6038-6R2Y
C_0603_1608Metric x 5
R_0805_2012Metric x 15
TB005-762-02P_Blue - S
C-1-1123723-2
BODY-TSSOP x 2
LEAD-TSSOP x 56
DAP x 2
JST_SH_BM04B-SRSS-TB_1x04-1MP_P1.00mm_Vertical
TestPoint_Bridge_Pitch3.81mm_Drill1.3mm
PinHeader_1x12_P254mm_Vertical
CAR_KP_8X8_D8.5L9S3.5F0.65
adbeea53-9c39-11ed-93f0-dde97e994e83_part x 2
adbeea54-9c39-11ed-93f0-dde97e994e83_part x 2
adbeea55-9c39-11ed-93f0-dde97e994e83_part x 2
PinHeader_1x10_P254mm_Vertical
TB0011-350-03GR
D_SOD_123F x 4
C_1210_3225Metric
LED_D5.0mm
TC0403620000G
C_1206_3216Metric
LED_D3.0mm
RaspberryPi_Pico_Module_KiCad
375424B00034G x 2
gbg-pcb_PCB

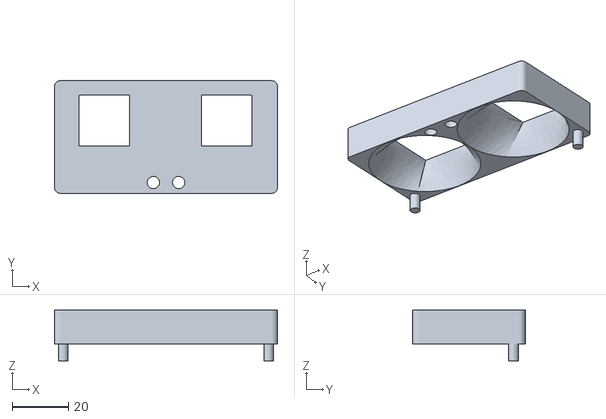
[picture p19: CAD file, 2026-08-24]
case/gbg-pcb-case-fan-funnel.stl
79.2 x 40.0 x 18.0

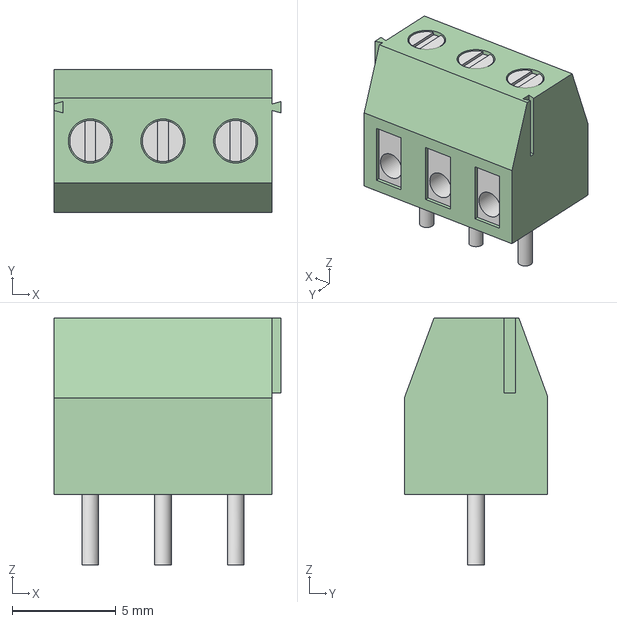
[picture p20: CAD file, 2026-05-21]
kicad/kicad libraries/TB0011-350-03GR.stp
10.9 x 6.90 x 11.9 mm

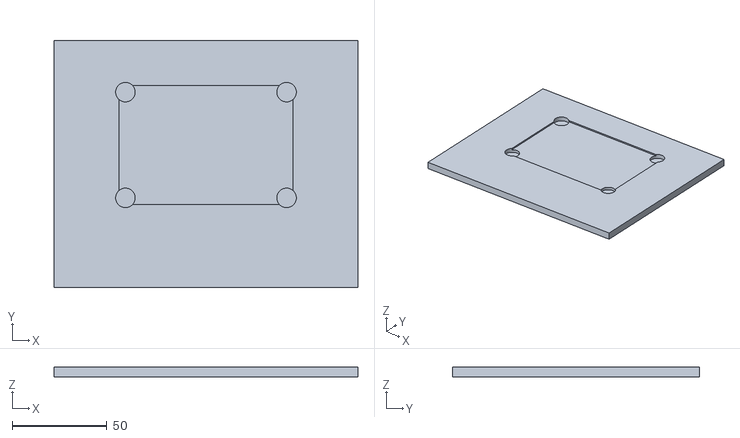
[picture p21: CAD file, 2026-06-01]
PCB_production/stencil-jig.stl
160.0 x 130.0 x 5.00

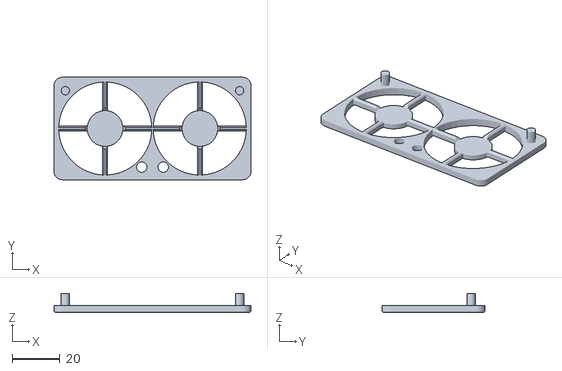
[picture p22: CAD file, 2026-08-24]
case/gbg-pcb-case-fan-cover.stl
82.5 x 43.0 x 8.00

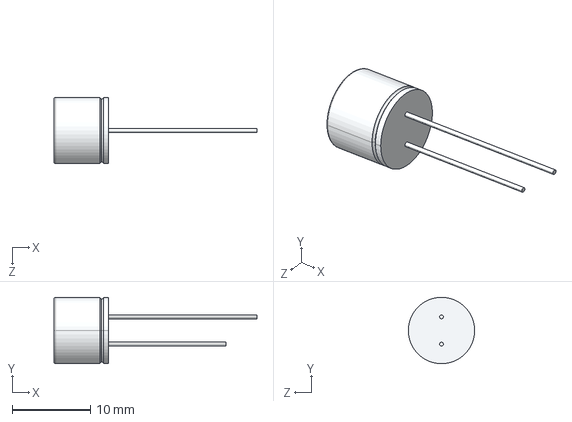
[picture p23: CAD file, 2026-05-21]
kicad/kicad libraries/A759KC276M1JAAE054.step
26.0 x 8.50 x 8.50 mm

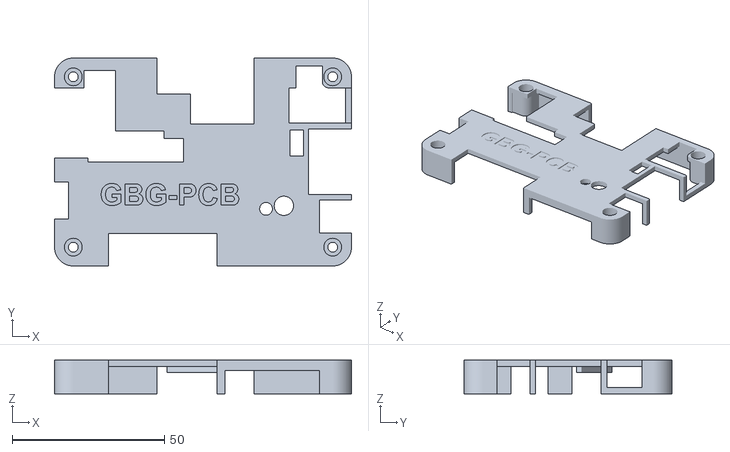
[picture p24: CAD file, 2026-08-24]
case/gbg-pcb-case-top.stl
97.4 x 68.2 x 11.0

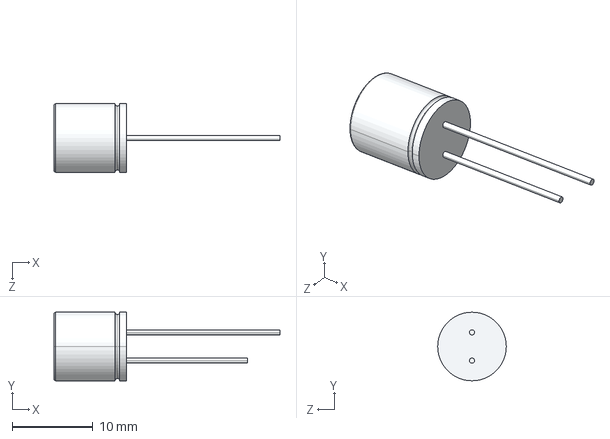
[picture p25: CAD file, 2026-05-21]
kicad/kicad libraries/A759KK336M1JAAE036.step
28.0 x 8.50 x 8.50 mm

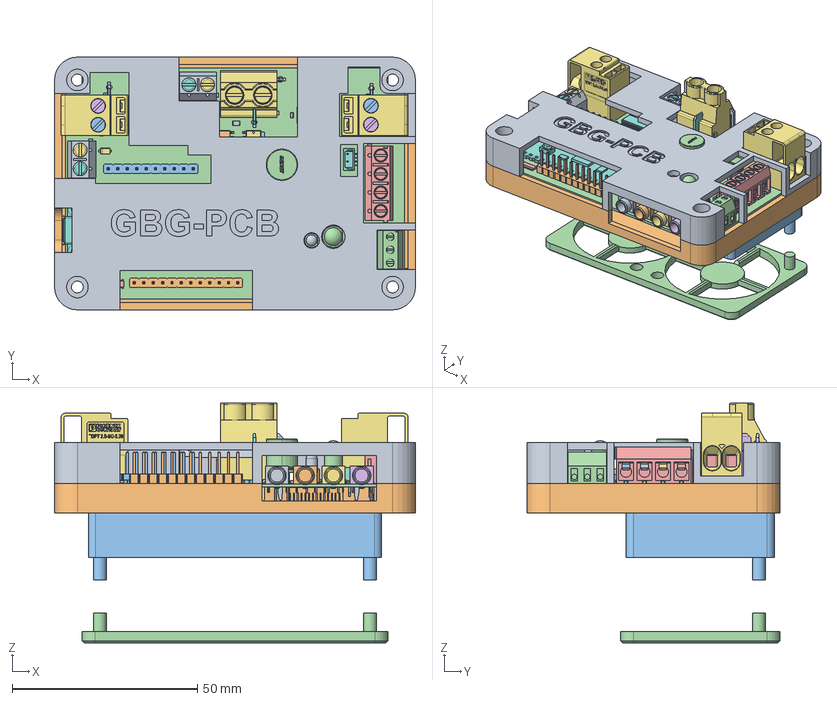
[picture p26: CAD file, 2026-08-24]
case/case.FCStd
97.4 x 68.2 x 64.7 mm
top
bottom
fan-funnel
fan-cover
Pins
Pins001
Pins002
Pins003
Pins004
Pins005
Pins006
Pins007
Pins008
Pins009
Pins010
Pins011
Pins012
Pins013
Pins014
Pins015
ADS1115IRUGR013
ADS1115IRUGR014
ADS1115IRUGR015
ADS1115IRUGR016
ADS1115IRUGR017
ADS1115IRUGR018
ADS1115IRUGR019
ADS1115IRUGR020
ADS1115IRUGR021
ADS1115IRUGR022
ADS1115IRUGR023
ADS1115IRUGR024
ASJ-200-B-HT008
EBBA-02-C-SS-BU016
EBBA-02-C-SS-BU017
EBBA-02-C-SS-BU018
EBBA-02-C-SS-BU019
EBBA-02-C-SS-BU020
EBBA-02-C-SS-BU021
EBBA-02-C-SS-BU022
SRR6038-6R2Y004
SRR6038-6R2Y005
SRR6038-6R2Y006
C_0603_1608Metric010
R_0805_2012Metric030
TB005-762-02P_Blue - S001
C-1-1123723-001
BODY-TSSOP002
LEAD-TSSOP056
LEAD-TSSOP057
LEAD-TSSOP058
LEAD-TSSOP059
LEAD-TSSOP060
LEAD-TSSOP061
LEAD-TSSOP062
LEAD-TSSOP063
LEAD-TSSOP064
LEAD-TSSOP065
LEAD-TSSOP066
LEAD-TSSOP067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

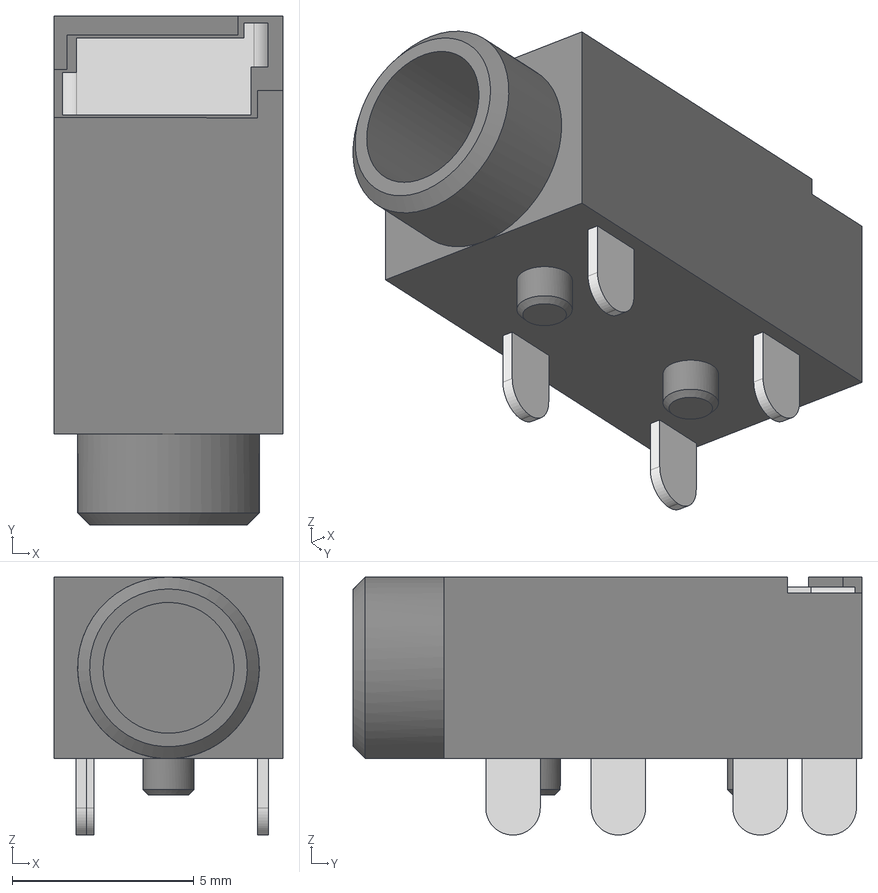
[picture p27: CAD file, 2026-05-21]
kicad/kicad libraries/ASJ-200-B-HT.stp
6.30 x 14.0 x 7.10 mm

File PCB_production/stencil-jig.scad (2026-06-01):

// gbg-pcbs can be set into the cutout of this panel to hold them still while applying solder paste.
// Dimensions
in2mm=25.4;
block_width = 160;
block_height = 130;
block_thickness = 5;

// Cutout dimensions
cutout_thickness=1.0;

cutout_width = in2mm*(3.6+.01);
cutout_height = in2mm*(2.45+.01);
corner_radius = in2mm*(0.125+.01);

// Smoothness of rounded corners
$fn = 64;

difference() {
    // Main rectangle block
    cube([block_width, block_height, block_thickness]);

    // Rounded rectangle cutout
    translate([
        (block_width - cutout_width) / 2,
        (block_height - cutout_height) / 2 + 10,
        block_thickness-cutout_thickness
    ]){
        linear_extrude(height = block_thickness){
            rounded_rectangle(cutout_width, cutout_height, corner_radius);
        }
        translate([0,0,-2])
        linear_extrude(height = 2*2){
            corner_circles(cutout_width, cutout_height, corner_radius,1.5);
        }
    }
}

// 2D rounded rectangle module
module rounded_rectangle(w, h, r) {
    hull() {
        translate([r, r]) circle(r);
        translate([w - r, r]) circle(r);
        translate([r, h - r]) circle(r);
        translate([w - r, h - r]) circle(r);
    }
}
module corner_circles(w,h,r,m){
    translate([r, r]) circle(r*m);
    translate([w - r, r]) circle(r*m);
    translate([r, h - r]) circle(r*m);
    translate([w - r, h - r]) circle(r*m);
}

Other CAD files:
kicad/kicad libraries/1017491.stp
kicad/kicad libraries/375424B00034G.stp
kicad/kicad libraries/63900-1--3DModel-STEP-1(1).STEP
kicad/kicad libraries/D78B05T-1.0.step
kicad/kicad libraries/TC0403620000G.stp
kicad/kicad libraries/sk_675_100_al.stp

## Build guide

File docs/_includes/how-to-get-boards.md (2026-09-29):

V2 GBG-PCBs can run from 6 to 24 volt batteries. V2 boards can also be [configured](https://gobabygocarswithjoysticks.github.io/gbg-pcb/instructions/instructions#new-in-v2-weelye-control-box-compatible) with battery, motor, and signal plugs that match the plugs on the common weelye control boxes. This means some cars can be converted to joystick control without cutting any wires. For the previous versions of the GBG-PCB see [https://github.com/gobabygocarswithjoysticks/gbg-pcb/tree/version_1](https://github.com/gobabygocarswithjoysticks/gbg-pcb/tree/version_1) 

Version 1 GBG-PCBs had a higher, (10+ amp) current capacity and a lower part count but only runs on 12 volts.

Options for How To Get Boards:

 a. Please feel free to use these [files](/PCB_production) and get boards yourself. There are instructions [here](https://gobabygocarswithjoysticks.github.io/gbg-pcb/instructions/how-to-make-boards/how-to-make-boards) for how to make GBG-PCBs by hand.

 b. [Use this PCBWay link to order fully assembled boards](https://www.pcbway.com/project/shareproject/GBG_PCB_Go_Baby_Go_Printed_Circuit_Board_V2_3_standard_e5a44837.html). Or, alternative PCBWay links if you want to complete the assembly yourself: [PCBWay can do everything but leave the battery and motor connectors off](https://www.pcbway.com/project/shareproject/GBG_PCB_Go_Baby_Go_Printed_Circuit_Board_V2_3_without_battery_and_motor_co_59a1961e.html) or, [PCBWay can do the challenging surface mount soldering and leave the through-hole soldering for you](https://www.pcbway.com/project/shareproject/GBG_PCB_Go_Baby_Go_Printed_Circuit_Board_V2_3_SMD_only_0de9c2fe.html)

 c. Email gobabygocarswithjoysticks@gmail.com. We may have a spare V1 or V2 GBG-PCB that we can sell or donate to you.
 
 d. Email pnwassistivetech@gmail.com or visit the [PNW Assistive Technology website](https://pnwassistivetechnology.org/plug-and-drive). Thank you to PNWAT for sponsoring V2 GBG-PCB prototyping runs and being a supplier of V1 and V2 GBG-PCBs (called "plug and drive boards" by PNWAT).

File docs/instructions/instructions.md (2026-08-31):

# Instructions for using the GBG-PCB to make a go baby go car

questions? post [here](https://github.com/gobabygocarswithjoysticks/gbg-pcb/discussions/categories/questions-and-troubleshooting) or email gobabygocarswithjoysticks@gmail.com 

# Instructions for specific models of cars
* [Aosom Jeep](https://gobabygocarswithjoysticks.github.io/gbg-pcb/instructions/car-specific/aosom-038-jeep/instructions)
* [Zupapa Bumper Car](https://gobabygocarswithjoysticks.github.io/gbg-pcb/instructions/car-specific/zupapa-bumper-car/instructions)
* [Flybar Bumper Car](https://gobabygocarswithjoysticks.github.io/gbg-pcb/instructions/car-specific/flybar-bumper-car/instructions)

# Parts needed
* a car
* materials for frame and backrest (usually pvc pipe)
* materials for modifying the car to spin in place (caster wheels)
* joystick (recommended part: Radiolink joystick replacement for RC controllers AT9 and AT10 (get the “back to middle” type that springs back on both axes) )
* four wire electrical cable - for joystick
* [3D printed parts](https://github.com/gobabygocarswithjoysticks/index?tab=readme-ov-file#cad) (handles, joystick holder)
* an assembled [joystickpcb](https://github.com/gobabygocarswithjoysticks/gbg-pcb/tree/main/joystickpcb)
* an assembled GBG-PCB
{% include how-to-get-boards.md %}
# Tools needed
* flathead screwdriver (3mm)
* small Phillips screwdriver (2.0)
* wire strippers
* wire cutters
* micro USB cable

# Circuit diagram
circuit diagram

## [Schematic of GBG-PCB](https://github.com/gobabygocarswithjoysticks/gbg-pcb/blob/main/schematic.pdf)
## [List Of Components to build a GBG-PCB](https://github.com/gobabygocarswithjoysticks/gbg-pcb/blob/main/PCB_production/BOM.csv)

## New in V2: Weelye control box compatible

Ride on cars frequently come with a control box labeled "weelye." The GBG-PCB can be configured with plugs that match the weelye box so that some models of cars can be modified without cutting any wires.

The plug carrying signal wires to the box can be plugged into J11 with the usually-red wire plugged into the pin labeled bat+ and if the plug from the car has fewer than 10 sockets leave the rightmost pins of the GBG-PCB unused.

A GBG-PCB can be assembled with alternate motor and battery connectors that are compatible with the plugs on weelye boxes.
[See section titled "alternate battery and motor connectors weelye mode" for what components to change.](https://github.com/gobabygocarswithjoysticks/gbg-pcb/tree/main/PCB_production#alternate-battery-and-motor-connectors-weelye-mode)

---

# Choose a Car
## 6 to 24 volts
While V1 boards required 12 volts, V2 GBG-PCBs can be used with 6 volt, 12 volt, or 24 volt cars.

## Two motors
### The car will be steered by controlling the two back wheels separately, so the car needs to have a motor for each wheel.

Cars with two speeds often have two motors in them.

Some cars are sold with one motor but have space in the frame to add a second motor. 

## Able to (be modified to) spin in place
### Some models already can spin in place ("bumper cars")
### For most cars, you'll need to remove the front wheels and add swivelling caster wheels.

## Fits a frame and has a way to connect a joystick
### Go Baby Go cars usually get a PVC pipe frame with a backrest
It's easier to fit a frame to a blockier car with more right angles
### The joystick can be connected to the frame, or it can be put on the end of an "adjustable photo arm"
[Here](https://github.com/gobabygocarswithjoysticks/index?tab=readme-ov-file#cad) are some 3D printed parts that could be used to hold the joystick.

---

# Disconnect the battery
### If possible, disconnect one wire from the battery to keep the circuit off while you are working on it. Some cars have a spade terminal that comes disconnected from the battery of a new car.

# Wire the PCB to the motors
## Find the motors
### The motors are usually under the seat of the car
## Prepare the motor wires
### Cut the plugs off the ends of the motor wires
### Strip the insulation off the ends of the wires
## Connect the motors to the PCB
### The motors can be reversed or swapped left/right in software later.

# Wire the PCB to the battery

If there is a plug that comes from the battery and goes to a circuit board that is already in the car, you can probably cut that plug off and use those wires to power the GBG-PCB. 

If you see a fuse (usually a small black box with two wires coming out of it), please leave it in the circuit between the battery and the GBG-PCB. It's a really good idea to have a fuse between the battery and the PCB; if you need to get a fuse, a 10 Amp auto resetting fuse is a reasonable choice.

Connect the positive battery wire (usually red) to the positive BATTERY terminal on the GBG-PCB (labeled "+"). 

Connect the negative battery wire (usually black) to the negative BATTERY terminal on the GBG-PCB (labeled "-"). 

The GBG-PCB has reverse voltage protection, so it won't be damaged if you accidentally connect the battery backwards. It just won't turn on.

### The PCB can be left connected to the battery. It does not need a switch between itself and the battery. The PCB has MOSFETs that stop electricity from flowing when the on/off switch is off. When the PCB is off it draws practically zero current (2 nanoAmps) so it will not make the battery discharge.

If your car has a switch that can handle the full current of the car, you can use that switch as the main power on/off switch and put it between the battery and the GBG-PCB. If you do this, connect the two terminals labeled "on/off" on the GBG-PCB together with a short wire.

# Wire the PCB to the on/off switch
## Choose or add a switch to use as the main power on/off switch.
### Low currents (about 4 mA) will flow through this circuit, so any wires and switches will work.
## Connect the switch to the screw terminal labeled on/off.
### Current can flow either way through a switch so either wire from the switch can go to either terminal.
### An electrical connection between the two terminals of the on/off screw terminal block will turn the PCB on.
It doesn't matter for a switch (and I recommend just using a regular switch), but in case you're interested, the terminal closer to the battery is connected to the positive wire of the battery and the terminal closer to the left motor should be pulled to 12 Volts to turn the board on. The MOSFETs interrupt the connection to the negative wire of the battery. The instructions specifically for the jeep describe how to use the button on the dashboard to turn the car on, and in that case the dashboard needs to be grounded directly to the battery or the signal from the button on the dashboard floats high and the car can't be turned off. The instructions specifically for the zupapa bumper car describe how to add the GBG-PCB in parallel to the existing control box and that strategy is helpful for cars with more complex wiring for the battery charger.

## V2 GBG-PCB on/off switch
Many cars have a multiple-wire harness that goes to a plug on the control box that the car comes with. Those wires contain the signal from the car's on/off switch and sometimes also carry power when charging the car. The J11 "weelye" header pins on the GBG-PCB are designed to connect to that plug so that the car can be charged and turned on and off as normal, replacing the control box completely. The usually-red wire from the car's plug goes to the pin labeled bat+ on the GBG-PCB and if the plug from the car has fewer than 10 sockets leave the rightmost pins of the GBG-PCB unused.

# Wire the Joystick
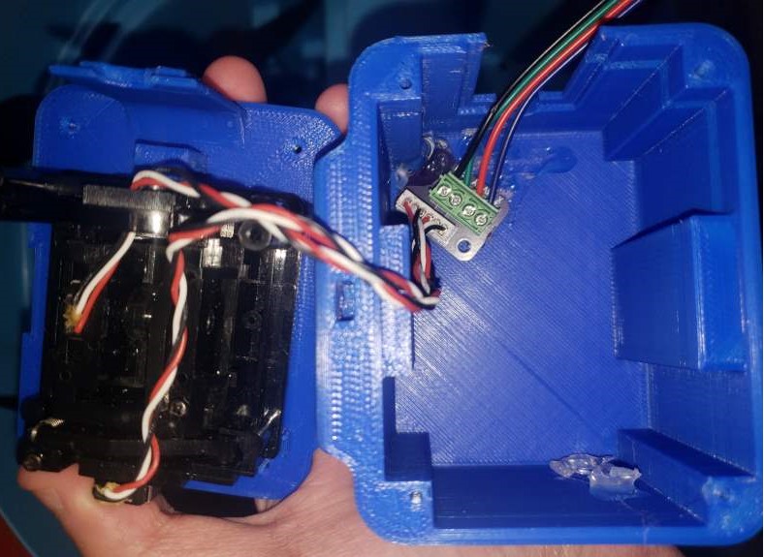
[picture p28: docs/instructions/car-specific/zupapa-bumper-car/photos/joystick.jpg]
joystick photo

Use a 4 wire cable to connect the GBG-PCB to the joystickpcb.

This picture shows the circuit but for illustration purposes the wires are very short. The wires should be long enough to reach from the PCB to wherever the joystick will be placed on the car and the wires should be long enough to be routed through the frame of the car.
# (optional) Wire Buttons and/or Speed Knob
## Buttons
Plug up to 4 buttons into the headphone-style jacks on the GBG-PCB.

When you connect the GBG-PCB to your computer to change the settings, click the "show all" button and check the box next to "enable button_ctrl". Then, you can set what direction each button should make the car move in.
## Speed Knob
You can add a knob to the car for easily adjusting the maximum speed of the car without needing to reprogram it.

Connect a potentiometer to the screw terminal labeled "speed knob". When you connect the GBG-PCB to your computer to change the settings, click the "show all" button and check the box next to "use speed knob".

# Program the Pico
## Flash the firmware to the Pico
If you got your GBG-PCB from someone who already programmed it for you, then you can skip ahead to calibrating the joystick and adjusting settings.

Go to [the go baby go programmer website](https://gobabygocarswithjoysticks.github.io/programmer/#new) and follow the instructions to upload code to a new car.

Select the PCB_gbg_program. If you don't see the PCB program, click on Advanced settings and check the box to get car code from the main branch.

## Connect
### Connect the GBG-PCB to your computer with a micro USB cable
### Go to [the go baby go programmer website](https://gobabygocarswithjoysticks.github.io/programmer/#configure)
### Follow the instructions pointed to with the magenta arrow to connect to the car
## Calibrate the joystick and adjust settings
### Click the "calibrate the joystick the easy way" button and follow the instructions on the screen
### You can also adjust the speed and acceleration settings for the car.

# Reconnect the battery
### If you disconnected a wire from the battery (or the car comes with a wire disconnected for shipping), reconnect it now.

# Test the car
## disconnect the car from the computer
## turn on the car using the on/off switch
### the three green lights on the PCB should turn on
### you should hear a short beep from the motors
## the car should drive when you move the joystick
### the blue light on the PCB should turn on when the car is moving and turn off when the joystick is centered
### if the blue light blinks quickly that means the joystick needs to be left centered for a few seconds before trying to move and that the joystick may need to be recalibrated

# Notes on remote control 
## See this page for several methods of remote control: [remote control](https://github.com/gobabygocarswithjoysticks/car-code/tree/main/rcdocs)

## Over wifi
This feature is available on GBG-PCBs with a Pico 1W or 2W.

Check the "use wifi" setting on the programmer website, then follow the instructions and QR codes on the programmer website.

The Pico will create a wifi network and will serve a webpage that allows you to control the car and change settings of the car.

The wifi range is unreliable (sometimes measured as 10 feet sometimes as 100 feet).

For more information, see the remote control page linked above.

# Troubleshooting
## If you would like help troubleshooting your car or if you have any questions, please email [gbg-pcb@googlegroups.com](gbg-pcb@googlegroups.com)
# The car doesn't drive in the direction the joystick is pointing in
#### follow these steps to reprogram the car if it drives in the wrong direction:
### 0. Connect the programmer website and calibrate the joystick
### 1. If moving the joystick forwards makes the car spin, use the website to reverse the motor that the car turned towards (show all the settings then press the reverse motor button next to the "motor fast" setting)
### 2. If moving the joystick forwards makes the car drive backwards, use the website to reverse both motors
### 3. If the car spins the opposite direction from the direction that the joystick is pointed, use the website to swap the motors
### 4. Repeat steps 1-3 until the car drives correctly
# The car doesn't drive
## if the large round blue light blinks quickly
#### that means the joystick needs to be left centered for a few seconds before trying to move or that the joystick may need to be recalibrated
## if the small round green light doesn't turn on
#### the battery might have been connected backwards. A backwards connection does not damage the board; the board just doesn't turn on.
#### the on/off switch might not be making a connection
#### the battery might be low
#### the battery might not be connected
#### the fuse might have tripped but it should reset itself after a few seconds

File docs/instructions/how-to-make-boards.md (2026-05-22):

# How To Make GBG-PCBs
(by hand!)

The files you need are here: [https://github.com/gobabygocarswithjoysticks/gbg-pcb/tree/main/PCB_production](https://github.com/gobabygocarswithjoysticks/gbg-pcb/tree/main/PCB_production)

## parts
* components ([see BOM and notes on this page](https://github.com/gobabygocarswithjoysticks/gbg-pcb/tree/main/PCB_production))
* GBG-PCB circuit boards
* components and boards for joystick adapter boards [see this page](https://github.com/gobabygocarswithjoysticks/gbg-pcb/tree/main/joystickpcb)

## tools
* GBG-PCB solder stencil
* hot plate for reflow soldering (minimum 100mm x 100mm and 300 degrees Celcius)
* solder paste (I used Chip Quik WS991SNL500T4)
* solder wire
* soldering iron
* solder paste squeegee, ideally it's as wide as the PCB (a metal or plastic scraper, or a plastic card all work well)
* masking tape
* metal tweezers
* needle nose pliers
* sink with hot water
* heat resistant surface for setting boards on to cool
* gloves
* fume extractor
* paper towels
* isopropyl alcohol
* brush
* (optional) container that can hold the PCB
* (optional) hairdryer or hot air tool
* (optional) magnifying glass or microscope

## Add solder paste
Secure the PCB to the table (I like to use other PCBs to make a frame around the board but any method like maybe a 3D printed jig could work)

Align the solder stencil so the holes in the stencil are perfectly aligned with the shiny pads of the PCB. 

Tape the top edge of the solder stencil to the table so that the stencil can be flipped up and down. Make sure that when the stencil is on the PCB it lays flat (this is why using PCBs of the same height work so well as a frame).

You can wear gloves so you don't get solder paste on your hands

Make a line of solder paste across the top of the solder stencil. Close the solder paste container as soon as you get paste out of it so that it does not dry out.

Squeegee the solder paste across the stencil

Lift the stencil up and inspect the pads of the PCB. There should be solder paste on each pad. Some bridging of pads is ok (especially on the rpi pico (P1) since when it melts it will separate. Use a paper towel and isopropyl alcohol to clean the PCB if you need to retry.

Lift the PCB out and set it aside. You can repeat the process to add solder paste to multiple boards. You can often scrape unused paste off the stencil and collect it on your squeegee and reuse it for a few boards.

## Place components
Placing components on multiple boards saves time compared to making each board one at a time.

Use tweezers to place all the surface-mount (marked as "smd" in the BOM) components in their places on the board. The solder paste will hold the components in place. Later, when the solder paste melts surface tension will align the components so it's ok if they're slightly out of alignment. Try to avoid touching or smearing the solder paste.

[here's an interactive site where you can check off parts as you place them in an image](https://gobabygocarswithjoysticks.github.io/gbg-pcb/ibom/ibom.html)

_thank you [qu1ck](https://github.com/openscopeproject/InteractiveHtmlBom) for this amazing tool_

## Reflow solder
You can put a fume extractor near the hot plate to catch the smoke that will be made when the solder paste melts.

Set the hotplate to 240C 480F and wait for it to reach temperature

Make sure you have the boards, tweezers (or needle nose pliers), and a heat resistant surface to put boards on to cool.

Carefully pick up the PCB with tweezers or needle nose pliers (needle nose pliers can be easier to hold for multiple minutes).

Hold the PCB as close to the hot plate as you can without touching or tilting the PCB. Hold the PCB there for 1 minute so that the PCB can slowly warm up.

Gently set the PCB on the hotplate. Slide the PCB fully onto the hotplate.

The following steps shouldn't take more than about 15 seconds.

The solder paste should melt and become shiny.

The board will slighly warp away from the hotplate so use the tweezers to push the edges down one at a time so every part of the board gets hot and all the solder paste has a chance to melt.

Watch all the components and when all of the solder paste has melted, gently slide the PCB slightly off the hotplate then grab it with the tweezers or pliers and lift it off the hotplate. While you're lifting it the solder is liquid so move it slowly.

Put the PCB on a heat resistant surface so it can cool. 

If you have more boards you can repeat this process while the hotplate is already at the right temperature.

## Clean SMD soldering
To remove solder flux residue wash your board in hot running water. (yes, really) 
According to the solder paste datasheet the water should be above 60 degrees Celsius

Shake the board dry as well as you can then either leave it to air dry or gently dry it with warm air from a hairdryer.

Make sure there's no water on the board before powering it on and testing it for the first time.

Alternatively, fill a container with isopropyl alcohol, submerge the board, and brush the solder flux residue away

## Hand solder through-hole components
Solder the through-hole (marked tht in the BOM) components using solder wire and a soldering iron. Place and solder the shortest components first and end with the tallest components so that the parts don't fall out when you flip the board upside down on the table to solder.

## Solder joystick PCB

Use a soldering iron to solder the two connectors to the joystick PCB as shown in the image on this page [https://github.com/gobabygocarswithjoysticks/gbg-pcb/tree/main/joystickpcb](https://github.com/gobabygocarswithjoysticks/gbg-pcb/tree/main/joystickpcb).

## Clean THT soldering
Use hot water and/or isopropyl alcohol.

Make sure there's no water on the board before powering it on and testing it for the first time.

## Final touches
Stick the heatsinks to the back of the board. Make sure the heatsinks are centered in the marked boxes so they don't touch any of the pins.

## Test

Connect power, a joystick, motors (even small ones can help you test), and a power switch to the GBG-PCB.

Go to the [go baby go programmer website](https://gobabygocarswithjoysticks.github.io/programmer/#new) and follow the instructions to upload code to a new car.

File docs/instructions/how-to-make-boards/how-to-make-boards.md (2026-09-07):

# How To Make GBG-PCBs
(by hand!)

The files you need are here: [https://github.com/gobabygocarswithjoysticks/gbg-pcb/tree/main/PCB_production](https://github.com/gobabygocarswithjoysticks/gbg-pcb/tree/main/PCB_production)

## parts
* components ([see BOM and notes on this page](https://github.com/gobabygocarswithjoysticks/gbg-pcb/tree/main/PCB_production))
* GBG-PCB circuit boards
* components and boards for joystick adapter boards [see this page](https://github.com/gobabygocarswithjoysticks/gbg-pcb/tree/main/joystickpcb)
* (optional) 3D printed case ([top](https://github.com/gobabygocarswithjoysticks/gbg-pcb/blob/main/case/gbg-pcb-case-top.stl), [bottom](https://github.com/gobabygocarswithjoysticks/gbg-pcb/blob/main/case/gbg-pcb-case-bottom.stl), 4 12mm M3 bolts, and 4 M3 nuts)
* (optional, fans can be used to cool the boards and increase the maximum current that the boards can supply) 3D printed "[fan funnel](https://github.com/gobabygocarswithjoysticks/gbg-pcb/blob/main/case/gbg-pcb-case-fan-funnel.stl)", "[fan cover](https://github.com/gobabygocarswithjoysticks/gbg-pcb/blob/main/case/gbg-pcb-case-fan-cover.stl)" 2 40mm M4 bolts, 2 M4 nuts, and 2 cooling fans (choose voltage compatible with your car) [5V, 3.5-6](https://www.digikey.com/en/products/detail/sunon-fans/MF40200V1-1000U-A99/6198712), [12V, 4.5-13.8](https://www.digikey.com/en/products/detail/sunon-fans/MF40201V1-1000U-A99/6198971), [24V 8-27.6](https://www.digikey.com/en/products/detail/sunon-fans/MF40202V1-1000U-A99/6198716)

## tools
* GBG-PCB solder stencil
* hot plate for reflow soldering (minimum 100mm x 100mm and 300 degrees Celsius)
* solder paste (I used Chip Quik WS991SNL500T4)
* solder wire
* soldering iron
* solder paste squeegee (a metal or plastic scraper, or a plastic card all work well, search "putty knife")
* masking tape
* fine tip tweezers
* needle nose pliers
* heat resistant surface for setting boards on to cool
* gloves
* fume extractor
* paper towels
* isopropyl alcohol
* brush
* container that can hold the PCB
* multimeter
* (optional) 3D printed [stencil jig](https://github.com/gobabygocarswithjoysticks/gbg-pcb/blob/main/PCB_production/stencil-jig.stl)
* (optional) magnifying glass or microscope

## Add solder paste
[video here](https://youtu.be/dTn8IFIFuZ0)

Secure the PCB to the table (you can use other PCBs to make a frame around the board and tape the frame to the table, or use a 3D printed jig that the PCB fits into).

Align the solder stencil so the holes in the stencil are perfectly aligned with the shiny pads of the PCB. 

Tape the top edge of the solder stencil to the frame so that the stencil can be flipped up and down. 

Make sure that when the stencil is on the PCB it lays flat. 

Make sure that the holes in the stencil are still perfectly aligned with the pads on the PCB.

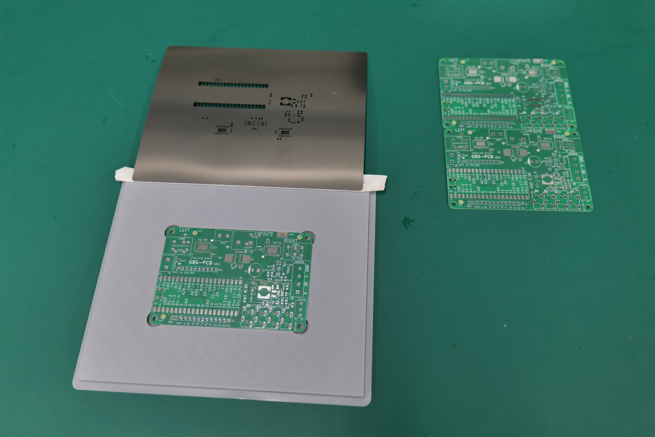
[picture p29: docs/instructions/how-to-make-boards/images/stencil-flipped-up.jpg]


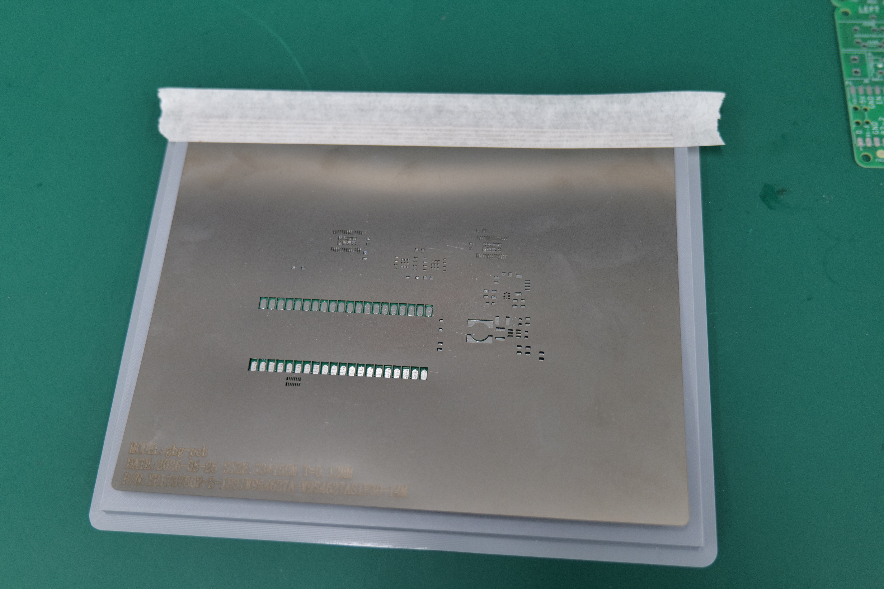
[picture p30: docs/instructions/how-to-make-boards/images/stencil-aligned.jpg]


You can wear gloves so you don't get solder paste on your hands

Make a line of solder paste across the top of the solder stencil. Close the solder paste container as soon as you get paste out of it so that it does not dry out.

Squeegee the solder paste across the stencil

Lift the stencil up and inspect the pads of the PCB. There should be solder paste on each pad. Some bridging of pads is ok (especially on the rpi pico (P1) since when it melts it will separate). Use a paper towel and isopropyl alcohol to clean the PCB if you need to retry. Pay special attention to R10 and U4.

Lift the PCB out of the frame and set it aside. You can repeat the process to add solder paste to multiple boards. You can scrape unused paste off the stencil and collect it on your squeegee and reuse it for a few boards.

## Place components
Placing components on multiple boards saves time compared to making each board one at a time.

Use tweezers to place all the surface-mount (marked as "smd" in the BOM) components in their places on the board. The solder paste will hold the components in place. Later, when the solder paste melts surface tension will align the components so it's ok if they're slightly out of alignment. Avoid touching or smearing the solder paste.

### [here's an interactive site where you can check off parts as you place them in an image](https://gobabygocarswithjoysticks.github.io/gbg-pcb/ibom/ibom.html)

_thank you [qu1ck](https://github.com/openscopeproject/InteractiveHtmlBom) for this amazing tool_

[video here](https://youtu.be/dwlZY8XkFCM)

## Reflow solder
[video here](https://youtu.be/GeIxBO7Buhc)

You can put a fume extractor near the hot plate to catch the smoke that will be made when the solder paste melts.

Set the hotplate to 240C 480F and wait for it to reach temperature

Make sure you have the boards, tweezers (or needle nose pliers), and a heat resistant surface to put boards on to cool.

Carefully pick up the PCB with tweezers or needle nose pliers (needle nose pliers can be easier to hold for multiple minutes).

Hold the PCB as close to the hot plate as you can without touching or tilting the PCB. Hold the PCB there for 1 minute so that the PCB can slowly warm up.

Gently set the PCB on the hotplate. Slide the PCB fully onto the hotplate.

The following steps shouldn't take more than about 20 seconds.

The solder paste should melt and become shiny.

The board will slightly warp away from the hotplate so use the tweezers to push the edges down one at a time so every part of the board gets hot and all the solder paste has a chance to melt.

Watch all the components and when all of the solder paste has melted, gently slide the PCB slightly off the hotplate then grab it with the tweezers or pliers and lift it off the hotplate. While you're lifting it the solder is liquid so move it slowly.

Put the PCB on a heat resistant surface so it can cool. 

If you have more boards you can repeat this process while the hotplate is already at the right temperature.

## Clean SMD soldering
Fill a container with isopropyl alcohol to a level that allows you to submerge the PCB.

Submerge the PCB in the isopropyl alcohol and use the brush to scrub the board around all soldered components. Take a minute of brushing to make sure you get all the solder flux off the board.

Alternatively, you can wash your board in hot running water. (yes, really)
According to the solder paste datasheet the water should be above 60 degrees Celsius. Make sure to dry the board well after washing it. You can use a hairdryer to help with this.

## Hand solder through-hole components
Solder the through-hole (marked tht in the BOM) components using solder wire and a soldering iron. Place and solder the shortest components first and end with the tallest components so that the parts don't fall out when you flip the board upside down on the table to solder.

## Solder joystick PCB
Use a soldering iron to solder the two connectors to the joystick PCB as shown in the image on this page [https://github.com/gobabygocarswithjoysticks/gbg-pcb/tree/main/joystickpcb](https://github.com/gobabygocarswithjoysticks/gbg-pcb/tree/main/joystickpcb).

## Clean THT soldering
Again, submerge the PCB in isopropyl alcohol and use the brush to scrub the board around all soldered components. If any joints don't look clean once the board dries you should put the board back in the isopropyl alcohol and brush those joints again.

A clean board looks better and is also less likely to corrode.

## Final touches
Stick the heatsinks to the back of the board. Make sure the heatsinks are centered in the marked boxes so they don't touch any of the pins.

## Test

Connect power, a joystick, motors (even small ones can help you test), and a power switch to the GBG-PCB.

Go to the [go baby go programmer website](https://gobabygocarswithjoysticks.github.io/programmer/#new) and follow the instructions to upload code to a new car. Make sure to select the PCB_gbg_program.

For more detailed instructions see [this page](https://gobabygocarswithjoysticks.github.io/gbg-pcb/instructions/instructions#flash-the-firmware-to-the-pico).

### Test the 5v tolerant pins
Pins 5,6,7, and 8 on the GBG-PCB are connected to a resistor voltage divider that allows the pico to read 5 volt signals. This is helpful for connecting remote control receivers that output 5 volt signals.
* On the programmer website, show all the settings, and check "use rc." 
* Use a multimeter to measure the voltage between ground and pins 5,6,7,8 on the Pico. 
* The voltages should read as approximately 0.25 volts. 
* If a pin reads as 3.3 volts or 0 volts, there is a problem with that pin and the soldering of R10 should be checked. 
* Then, uncheck "use rc."

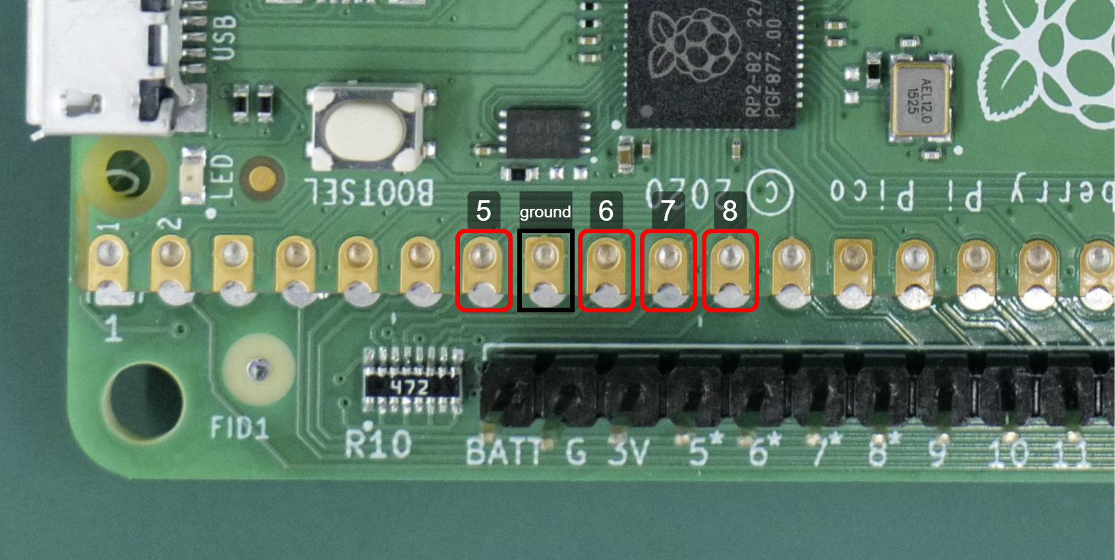
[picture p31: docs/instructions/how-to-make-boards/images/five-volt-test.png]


## Assemble the case

Assemble top and bottom 3D printed covers around the GBG-PCB using 4 12mm M3 bolts and 4 M3 nuts.

To add fans, add the 3D printed fan-funnel part, the two cooling fans, and assemble using 2 40mm M4 bolts and 2 M4 nuts. Note that the fans should be oriented so that they blow air onto the board, not pull air away from the board, so make sure the fans are oriented as shown in the image below.

case

Connect the red wire from each fan to the + side of the J6 "BATT" screw terminal and the black wire from each fan to the - side of the J6 "BATT" screw terminal so that the fans will turn on when the board turns on.

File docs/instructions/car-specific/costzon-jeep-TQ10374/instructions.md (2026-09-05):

Use a GBG-PCB to make a costzon jeep controlled by a joystick without needing to solder anything.

# Parts needed
* a 12 volt Costzon Jeep (TQ10374) [https://www.amazon.com/dp/B0FLY3R99N?th=1](https://www.amazon.com/dp/B0FLY3R99N?th=1)
    * These instructions are written specifically for this model of car. Other cars may have different circuits and require different steps. If you are using a different model, take a look at these [general instructions for using this PCB](https://gobabygocarswithjoysticks.github.io/gbg-pcb/instructions/instructions). A GBG-PCB can control most cars!
* an assembled [joystickpcb](https://github.com/gobabygocarswithjoysticks/gbg-pcb/tree/main/joystickpcb) (I'll include these with any GBG-PCBs that I give out)
* an assembled GBG-PCB ([part number](https://github.com/gobabygocarswithjoysticks/gbg-pcb/blob/main/PCB_production/part-numbers.md) GBG-PCB-V2.2-A2-B1-C1-D1W-E1-F1-G1-H1-J1-K1-L1-M1-N1-P1-Q1 is recommended to match the exact board these instructions are written with)

{% include how-to-get-boards.md %}

# Tools needed
* Phillips (+) screwdriver
* Wire strippers
* Wire cutters

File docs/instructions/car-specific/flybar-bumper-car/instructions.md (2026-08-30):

Use a GBG-PCB to make a Flybar bumper car controlled by a joystick without needing to solder anything.

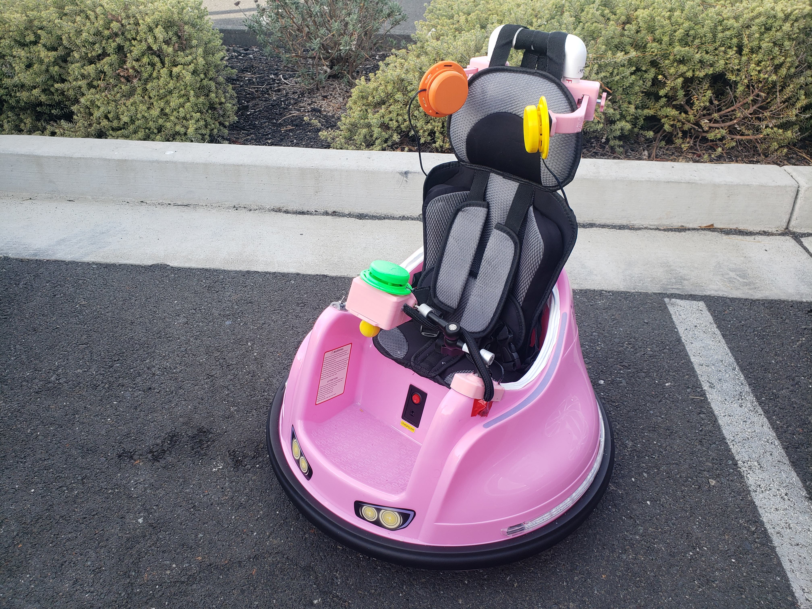
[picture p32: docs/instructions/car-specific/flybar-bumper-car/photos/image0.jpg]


questions? post [here](https://github.com/gobabygocarswithjoysticks/gbg-pcb/discussions/categories/questions-and-troubleshooting) or email gobabygocarswithjoysticks@gmail.com 

# Parts needed
* a 6 volt Flybar bumper car [https://www.flybar.com/products/flybar-bumper-car?variant=42204280881308](https://www.flybar.com/products/flybar-bumper-car?variant=42204280881308)
    * These instructions are written specifically for this model of car. Other cars may have different circuits and require different steps. If you are using a different model, take a look at these [general instructions for using this PCB](https://gobabygocarswithjoysticks.github.io/gbg-pcb/instructions/instructions). A GBG-PCB can control most cars!
* electrical tape
* PVC pipe
* 3 foot length of 4 wire electrical cable
* carseat harness
* adhesive backed velcro
* (if the car will have a joystick) 
    * 7 inch 20 pound capacity articulating photo arm
    * two 1/4-20 threaded heat set inserts
    * 4 m2.2x14mm screws
    * 1 foot length of fabric wire protector
    * 2 large zipties
    * Radiolink joystick replacement for RC controllers AT9 and AT10 (get the “back to middle” type that springs back on both axes)
* (if you will add headrest buttons to your car)
    * two 1 1/2 inch long 1/4-20 bolts with hex heads
    * two washers that fit the bolts
    * two 1/4-20 nuts

* 3d printed parts
    * set of [joystick holder](https://github.com/gobabygocarswithjoysticks/index/tree/flybar-bumper-car-v1/joystick-holder) parts printed in a color that matches the car
    * set of [joystick handles](https://github.com/gobabygocarswithjoysticks/index/tree/flybar-bumper-car-v1/joystick-balls) parts printed in a bright color that contrasts with the car
    * (if you will add a joystick to your car) [joystick holding arm mounting plate](https://github.com/gobabygocarswithjoysticks/index/tree/flybar-bumper-car-v1/joystick-holding-arm-mounting-plate) part printed in a color that matches the car
    * (if you will add headrest buttons to your car) [headrest button arms](https://github.com/gobabygocarswithjoysticks/index/tree/flybar-bumper-car-v1/headrest-button-holder) parts printed in a color that matches the car
    * [GBG-PCB case](https://github.com/gobabygocarswithjoysticks/gbg-pcb/tree/main/case) (just top and bottom, fans are not needed for this car)
* an assembled [joystickpcb](https://github.com/gobabygocarswithjoysticks/gbg-pcb/tree/main/joystickpcb) (I'll include these with any GBG-PCBs that I give out)
* an assembled GBG-PCB (screw terminal version recommended)

{% include how-to-get-boards.md %}

# Tools needed
* flush wire cutters
* wire strippers
* Phillips screwdriver
* small (3mm) flathead screwdriver
* small (2.0) Phillips screwdriver
* t6 torx screwdriver
* micro USB cable
* pvc pipe cutter or saw
* ductape
* hotglue
* JB Weld steel reinforced epoxy, or other gap-filling epoxy for plastic and PVC
* gloves
* drill
* 1/4 inch drill bit
* 28mm hole saw

# Instructions:

## Unpack the car
The car should have the two drive wheels and the two swivel wheels already connected.

Find the battery charger and set it aside for later.

## Modify the car's wiring

### Open the bottom panels of the car
Tilt the car on its back.

Unscrew all the screws holding the two halves of the car's bottom shell on.

Save all the screws for later.

Set the bottom panels aside.

Duct tape the black metal bar that holds the axel, motors, and wheels to the car.so that it doesn't fall out when you flip the car back upright.

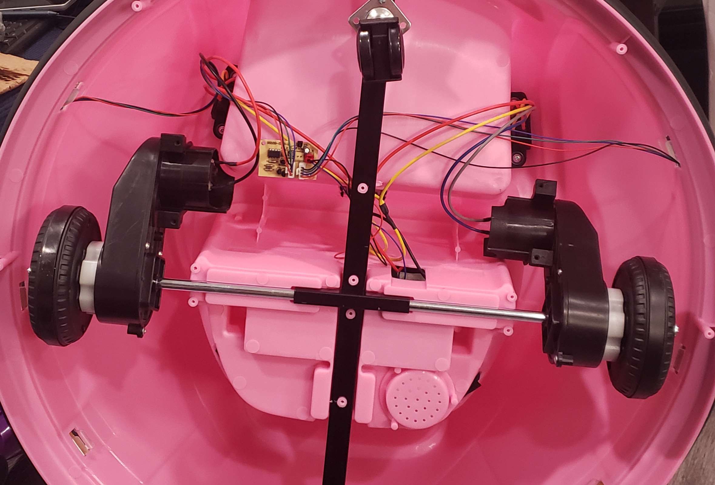
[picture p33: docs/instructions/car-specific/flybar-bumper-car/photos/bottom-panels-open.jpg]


### Cut motor wires
Use wire cutters to cut the red and black right motor wires as close as possible to the switch. The wires that are still attached to the motor needs to be long enough to reach under the seat.

Use wire cutters to cut the blue and grey left motor wires as close as possible to the switch.

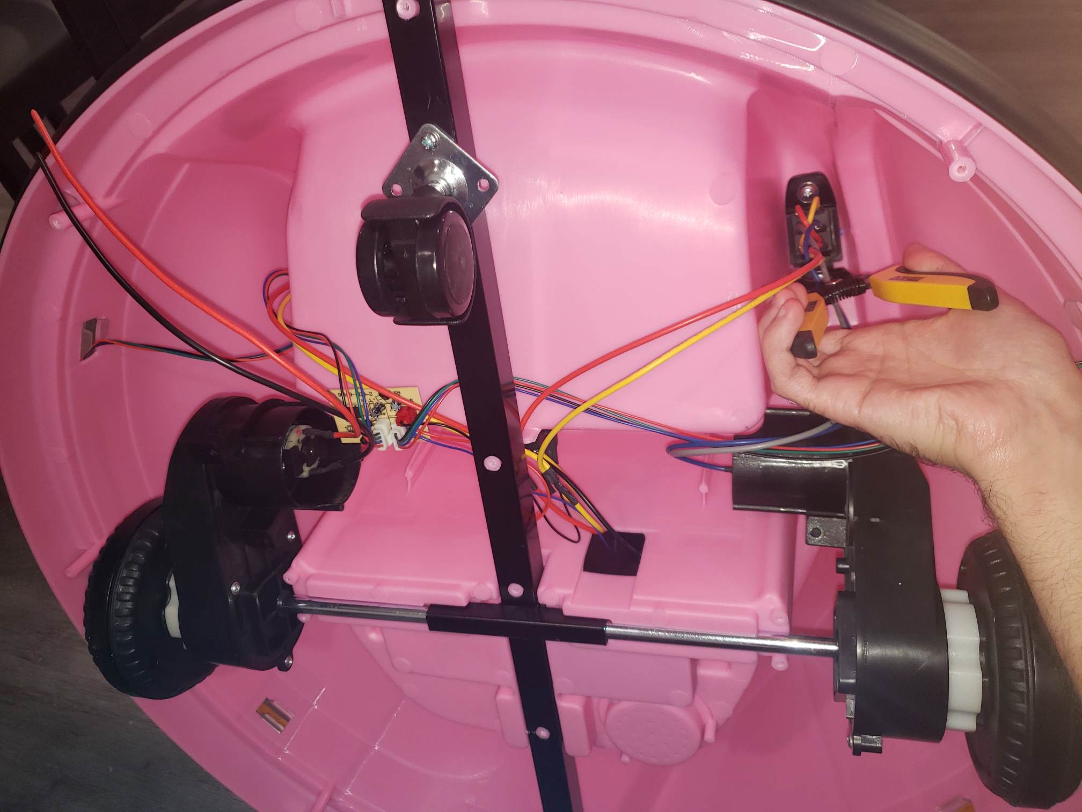
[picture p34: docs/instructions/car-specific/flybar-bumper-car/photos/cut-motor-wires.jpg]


### Cut battery wires
#### ! note !
Cutting wires connected to a battery can potentially be dangerous, but it's easy to do safely. Follow these three rules as you modify the car.

1. Keep the battery disconnected. The red wire comes disconnected from the battery. Leave it disconnected until the end. Cover the battery's terminal with electrical tape.
2. Make sure the on/off switch is in the off position.
3. Don't let the thick red wires touch the thick yellow wires. Never cut a red and yellow wire at the same time. Put electrical tape on the ends of yellow (ground) wires when you cut them.

Cut the yellow wire from one of the switches. Put electrical tape on the end of the wire.

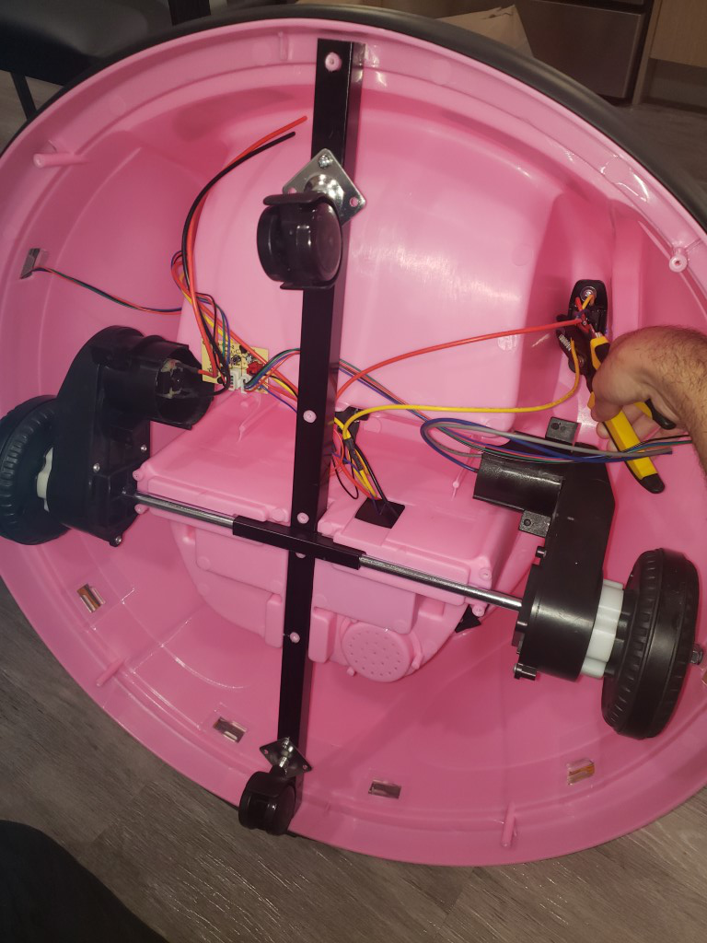
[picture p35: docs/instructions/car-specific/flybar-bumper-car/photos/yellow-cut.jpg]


Where the yellow wire branches into two, cut the wire that goes to the other switch. Wrap the junction in electrical tape to insulate the end of the stump of the wire.

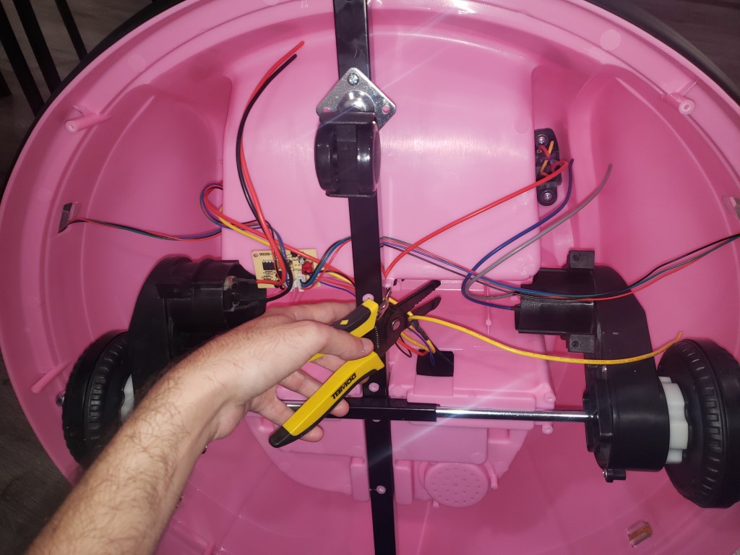
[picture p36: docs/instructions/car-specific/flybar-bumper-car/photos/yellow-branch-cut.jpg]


Cut the red wire from one of the switches.

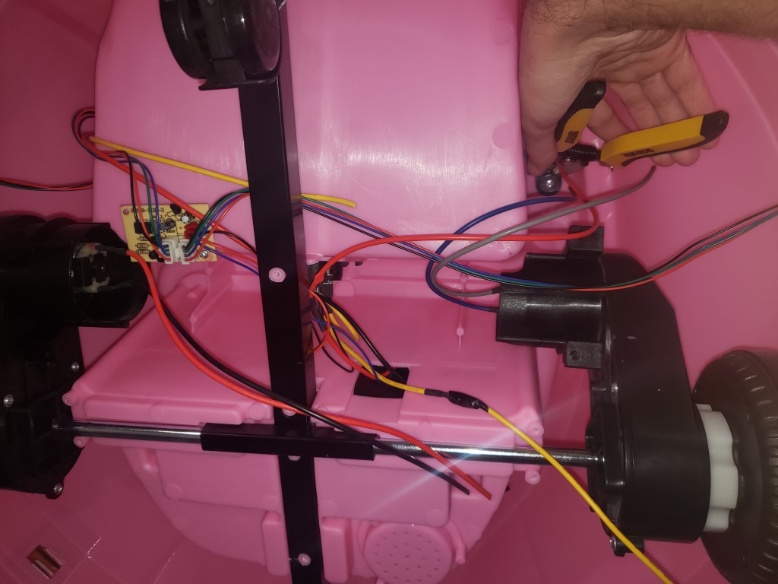
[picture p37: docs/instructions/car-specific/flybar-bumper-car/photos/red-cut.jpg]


Where the red wire branches into two, cut the wire that goes to the other switch. Wrap the junction in electrical tape.

At this point there should be two wires from each motor and two wires that come from the battery. All six of these wires need to be long enough to reach under the seat. Stick all the wires under the seat.

### Remove the switches
The two switches should have all their wires cut but may have some wires still hanging from them. 

Remove the pair of screws holding each switch to the car and discard the switches.

The handles are left, stuck inside the car. 

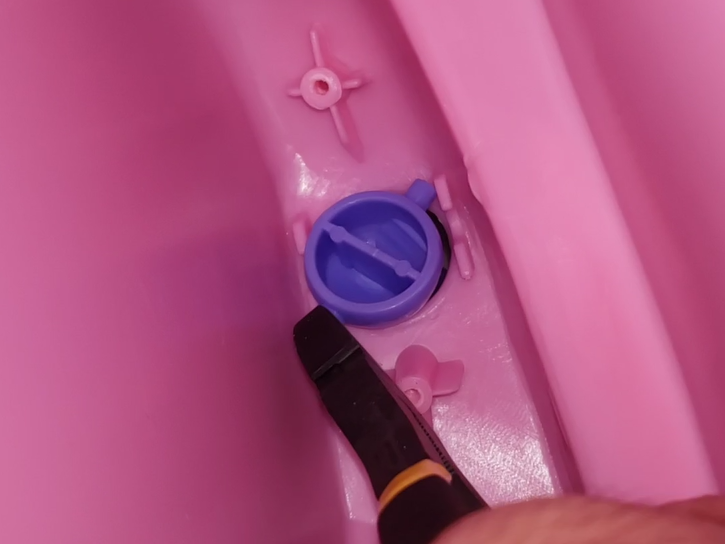
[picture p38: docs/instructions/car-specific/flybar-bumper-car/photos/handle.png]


Use a flush wire cutter to cut one of the plastic pegs off the handle. Then, pull the handle out of the car and discard it. Repeat for the other handle.

### Connect the GBG-PCB

Using a short length of wire (you can cut an inch off of a scrap of wire that you have now removed from the car, or use any other wire you have), strip 1/4 of an inch of wire off of each end and connect the two terminals of the switch screw terminal together. In this model of car the GBG-PCB will be turned on and off by the car's main switch connecting and disconnecting the battery, so the internal switching feature of the GBG-PCB is not needed.

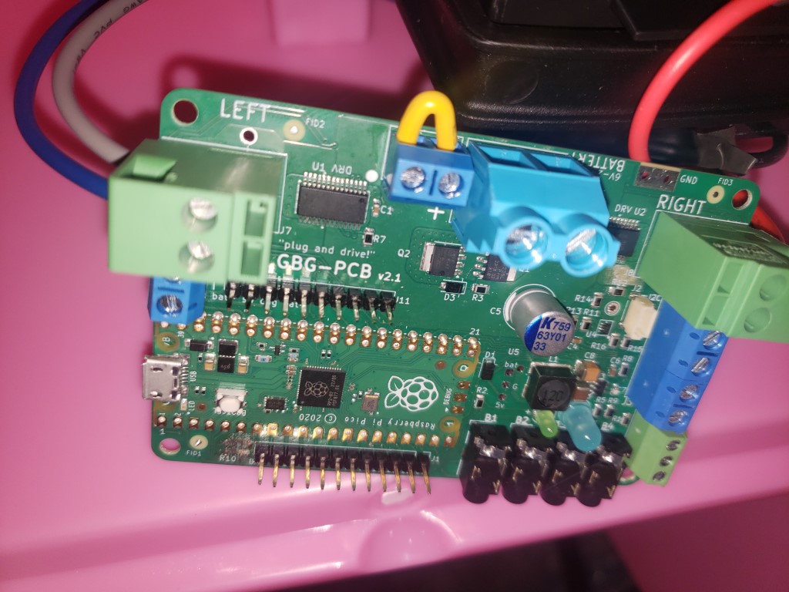
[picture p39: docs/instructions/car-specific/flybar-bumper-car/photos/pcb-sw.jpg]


Connect the red and black wires from the right motor to the right motor terminals on the GBG-PCB. The red wire goes to the terminal closer to the edge of the board and the black wire goes to the bottom terminal.

Connect the blue and grey wires from the left motor to the left motor terminals on the GBG-PCB. The blue wire goes to the terminal closer to the edge of the board and the grey wire goes to the bottom terminal.

Connect the red and yellow wires from the battery to the battery terminals on the GBG-PCB. The red wire goes to the left + terminal and the yellow wire goes to the right - terminal.

### Reconnect the battery
The cars are sold with a red wire disconnected from the battery to keep the car from turning on during shipping. This also made it safer to work on the electrical system. Now that you're done with the high-power wiring, you can make sure the power switch is in the off position then connect the red wire to the battery.

## Joystick

### Add the Joystick wires
Connect the 4-wire cable to the joystick terminals on the GBG-PCB. The standard coloring is X=blue, 3V=red, Y=green, gnd=black.

Route the 4-wire cable through the hole that the motor wires go through.

In the side of the left armrest, at least an inch from the top of the armrest (so it doesn't interfere with the arm mounting plate), drill a 1/4 inch hole for the 4-wire cable and thread the cable through the hole.

Put a fabric wire protector around the 4-wire cable to protect it from being broken if a kid pulls on the cable. The wire protector should be long enough to reach from the hole in the armrest to the joystick box.

Drill two 1/4 inch holes in the top of the left armrest, one on each side of the hole for the 4-wire cable. Use a ziptie to secure the wires and wire protector to the armrest.

### Assemble the joystick box
Add a 1/4-20 threaded heat set insert to the 3d printed joystick holder part.

Plug the joystick into the joystick pcb.

Connect the 4 wire cable to the screw terminal on the joystick pcb. Strip 1/4" (6 mm) of insulation off the ends of the wires and connect them to the screw terminal on the joystick pcb.

Hot glue the joystick pcb inside the 3d printed joystick holder so that it can't move around and jam the joystick. Match the position in the photo below.

Add a ziptie to the end of the wire protector, to keep the wires from being pulled out.

joystick pcb photo

Screw the top of the joystick holder to the bottom of the joystick holder, using 4 m2.2x14mm screws. If the joystick is incorrectly rotated, the 3d printed parts won't fit together. The ziptie and wire protector should be inside the joystick holder.

Use 4 m2.2x14mm screws to assemble the top and bottom of the joystick holder around the joystick.

## Button controls (optional)
Plug up to 4 buttons into the headphone-style jacks on the GBG-PCB. Route the wires through the hole in the right armrest.

When you connect the GBG-PCB to your computer to change the settings, click the "show all" button and check the box next to "enable button ctrl". Then, you can set what direction each button should make the car move in.

## Add the printed part that holds the arm that holds the joystick

Add a 1/4-20 threaded heat set insert to the 3d printed joystick holding arm mounting plate

Epoxy the mounting plate to the left armrest.

Tape the plate so the epoxy can cure.

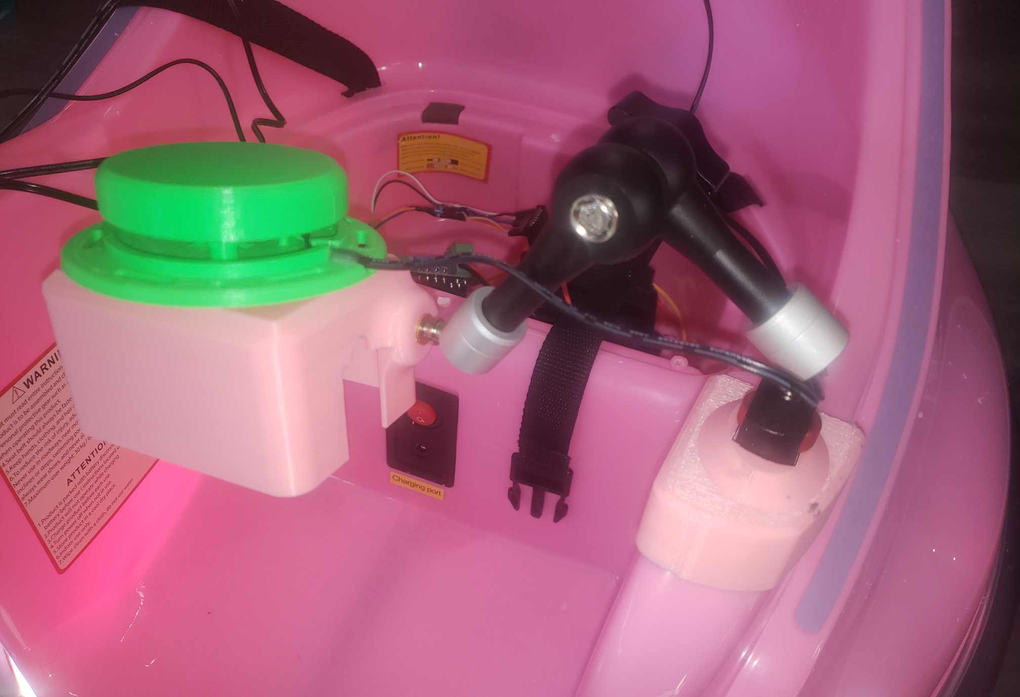
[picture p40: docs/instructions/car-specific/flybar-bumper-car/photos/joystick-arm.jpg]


## Add the backrest

Re-install the seat of the car.

Drill two 28mm holes in the top edge of the car's backrest. The holes should not cut through the wall that the kid will be leaning against but should be as close as possible to that wall. The holes should be a few inches apart. See the picture below for reference.

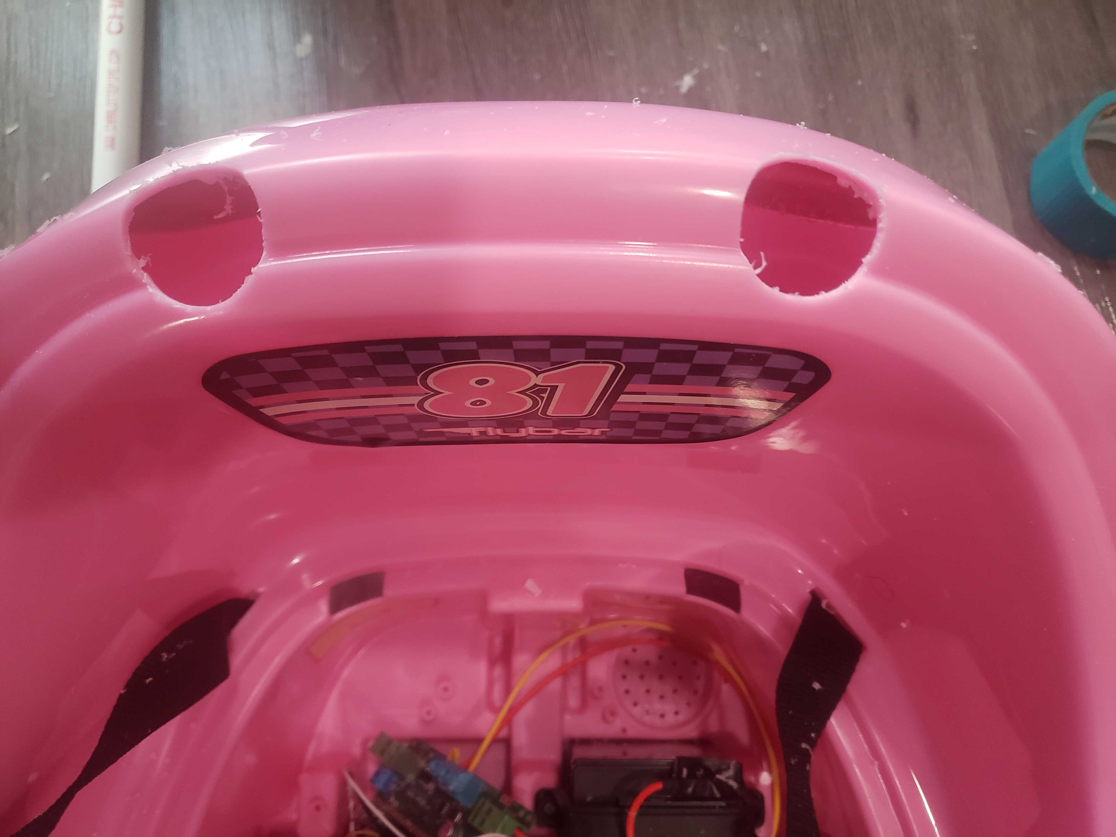
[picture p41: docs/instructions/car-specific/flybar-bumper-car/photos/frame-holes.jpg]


The PVC pipe backrest is a tall rectangle with 4 pipe elbows at the corners.

### Add the headrest button holders (optional)
Use a 1/4-20 bolt, washer, and nut to assemble each of the headrest arms, holders, and knobs. Add the holders to the longer PVC pipes of the backrest.

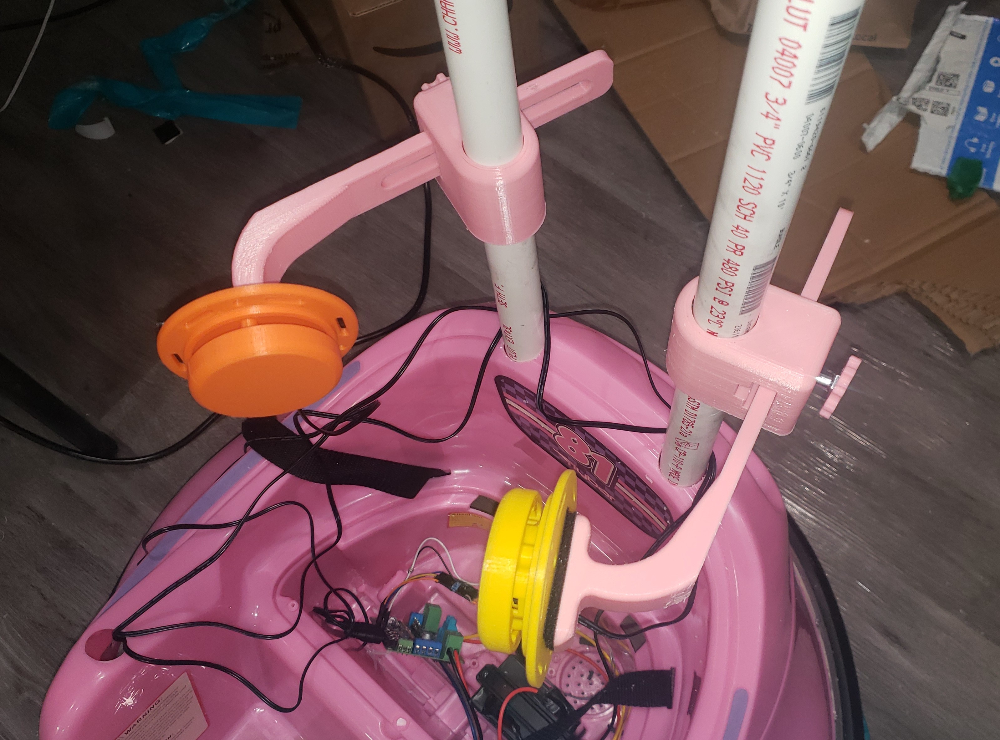
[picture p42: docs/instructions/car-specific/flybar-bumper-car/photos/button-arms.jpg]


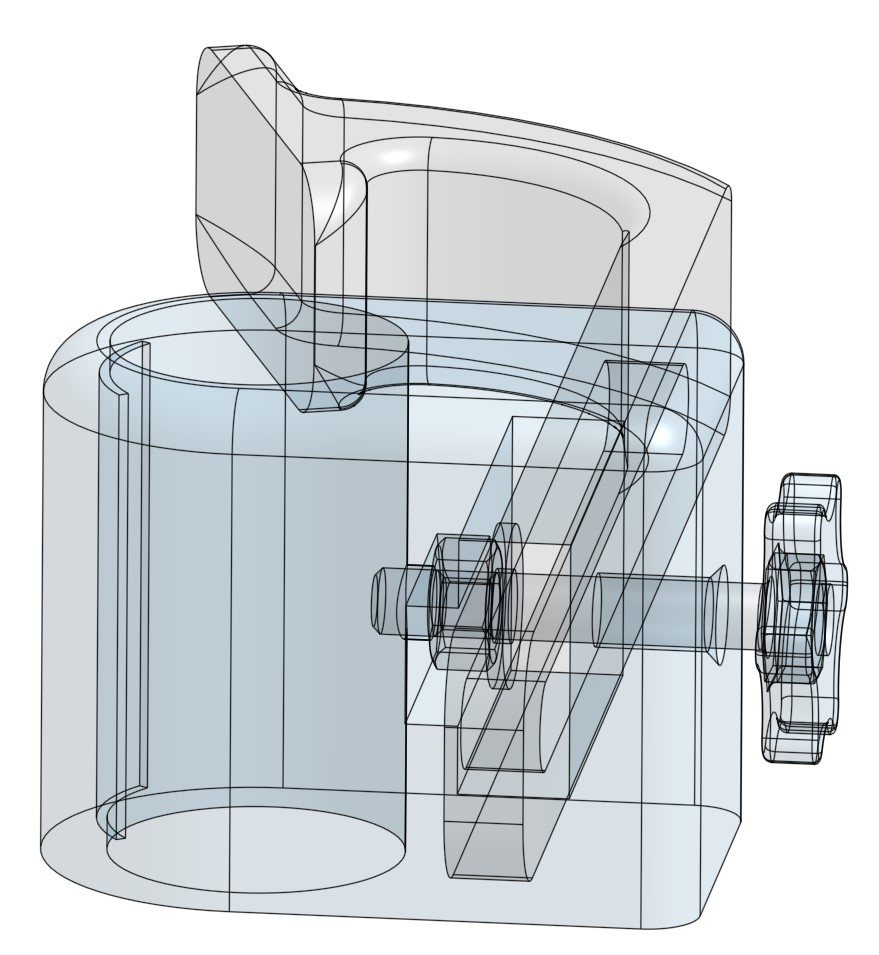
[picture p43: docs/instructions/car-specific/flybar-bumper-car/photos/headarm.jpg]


Use epoxy to glue the two bottom elbows to the back of the car. This can get a bit messy but make sure to keep the epoxy off the vertical pipes since those should be removable. Tape the assembly in place and let the epoxy cure.

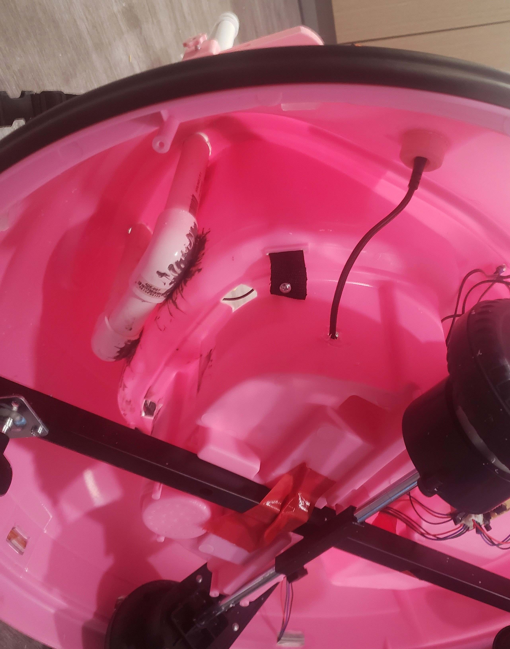
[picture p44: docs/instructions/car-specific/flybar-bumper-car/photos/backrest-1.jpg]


### Wait 24 hours for all the epoxy to cure.

### Re-attach the bottom panels of the car
Use the screws you saved to re-attach the bottom panels of the car.

# Software and Settings
## Flash the firmware to the Pico
If you got your GBG-PCB from someone who already programmed it for you, then you can skip ahead to calibrating the joystick and adjusting settings.

Go to [the go baby go programmer website](https://gobabygocarswithjoysticks.github.io/programmer/#new) and follow the instructions to upload code to a new car. Select the __PCB_gbg_program__ not the standard __gbg_program__.

## Connect
### Connect the GBG-PCB to your computer with a micro USB cable
### Go to [the go baby go programmer website](https://gobabygocarswithjoysticks.github.io/programmer/#configure)
### Follow the instructions pointed to with the magenta arrow to connect to the car
## Calibrate the joystick and adjust settings
### Click the "calibrate the joystick the easy way" button and follow the instructions on the screen
### You can also adjust the speed and acceleration settings for the car.

# Test the car
## disconnect the car from the computer
## turn on the car using the on/off button on the dashboard
### the three green lights on the PCB should turn on
### you should hear a short beep from the motors
## the car should drive when you move the joystick
### the blue light on the PCB should turn on when the car is moving and turn off when the joystick is centered
### if the blue light blinks quickly that means the joystick needs to be left centered for a few seconds before trying to move and that the joystick may need to be recalibrated

# final assembly

## Add the harness
Wrap the straps around the top tube of the backrest

Velcro the bottom of the harness to the seat.

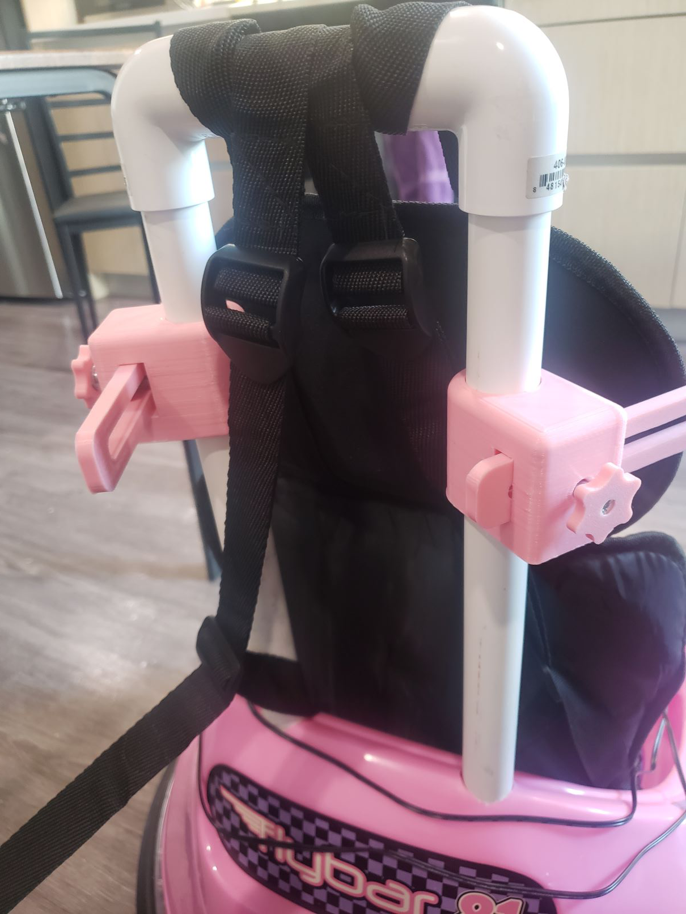
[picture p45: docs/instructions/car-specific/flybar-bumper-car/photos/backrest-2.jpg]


## Connect the joystick holder to the armrest

Once the epoxy for the mounting plate has dried, screw the 7 inch articulating photo arm to the mounting plate

# last steps

Print a [user guide](https://docs.google.com/document/d/1Bs-vC-6tTBjuLHyOXnoEMVlxUui_dN44Ry9QZwv9MxY/edit?usp=sharing) for the car.

Label the "on/off" button (the red switch on the control panel)

### Congratulations! You're done!

# Check your work
Check your work with this [inspection checklist](https://docs.google.com/document/d/1Nm6jOH3vKglHpVaZJPOpi3INnZ5qNjXhelSU0B2T-GE/edit?usp=sharing)

# Troubleshooting

## If you would like help troubleshooting your car or if you have any questions, please email gobabygocarswithjoysticks@gmail.com

# The car doesn't drive in the direction the joystick is pointing in
#### follow these steps to reprogram the car if it drives in the wrong direction:
### 0. Connect the programmer website and calibrate the joystick
### 1. If moving the joystick forwards makes the car spin, use the website to reverse the motor that the car turned towards (show all the settings then press the reverse motor button next to the "motor fast" setting)
### 2. If moving the joystick forwards makes the car drive backwards, use the website to reverse both motors
### 3. If the car spins the opposite direction from the direction that the joystick is points, use the website to swap the motors, then repeat the 3 steps starting at step 1
# The car doesn't drive
## if the blue light blinks quickly
### that means the joystick needs to be left centered for a few seconds before trying to move (this is a safety feature)
#### Let go of the joystick for 5 seconds and wait for the light to stop blinking
### it could also mean that the joystick needs to be recalibrated
#### If the blue light continues to blink quickly after letting go of the joystick for 5 seconds, then you should recalibrate the joystick using the programmer website. Connect the GBG-PCB to your computer, go to the programmer website, connect the website to the GBG-PCB, then click the "calibrate the joystick the easy way" button and follow the instructions on the screen.
## if none of the green lights on the PCB turn on,
#### the battery might have been connected backwards. A backwards connection does not damage the board; the board just doesn't turn on.
#### the on/off switch might not be wired correctly
#### the battery might need to be charged

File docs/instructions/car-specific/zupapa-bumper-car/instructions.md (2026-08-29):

Use a GBG-PCB to make a Zupapa bumper car controlled by a joystick without needing to solder anything.

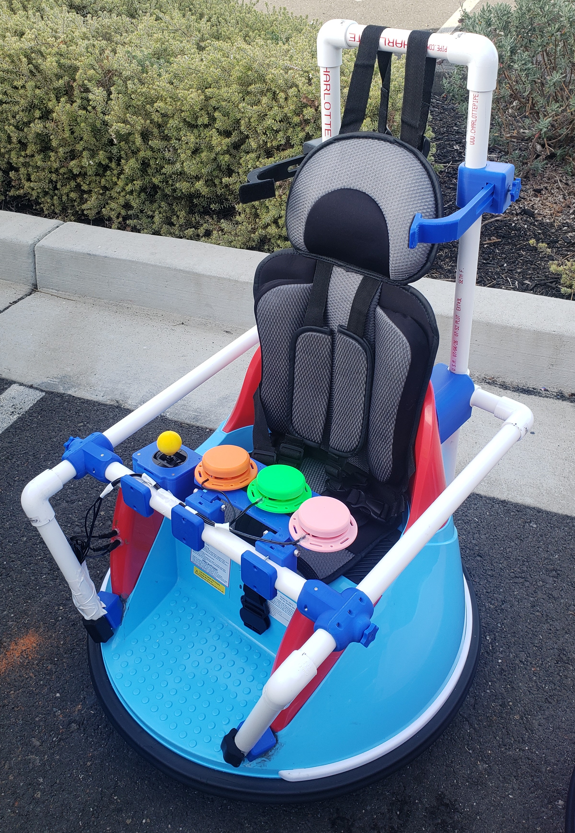
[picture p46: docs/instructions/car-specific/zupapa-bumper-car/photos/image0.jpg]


questions? post [here](https://github.com/gobabygocarswithjoysticks/gbg-pcb/discussions/categories/questions-and-troubleshooting) or email gobabygocarswithjoysticks@gmail.com 

## [Playlist of Videos for these instructions](https://www.youtube.com/playlist?list=PLt7UPvzv7L7Fb3U2_fuYpHY5yMrvgbvhL)

# Parts needed
* a 12 volt Zupapa bumper car [https://www.amazon.com/dp/B0CLLW3FBG?th=1](https://www.amazon.com/dp/B0CLLW3FBG?th=1)
    * These instructions are written specifically for this model of car. Other cars may have different circuits and require different steps. If you are using a different model, take a look at these [general instructions for using this PCB](https://gobabygocarswithjoysticks.github.io/gbg-pcb/instructions/instructions). A GBG-PCB can control most cars!
* 3 foot length of 4 wire electrical cable
* Radiolink joystick replacement for RC controllers AT9 and AT10 (get the “back to middle” type that springs back on both axes)
* 3d printed parts
    * set of [joystick holder](https://github.com/gobabygocarswithjoysticks/index/tree/zupapa-bumper-car-v1/joystick-holder) parts
    * set of [joystick handles](https://github.com/gobabygocarswithjoysticks/index/tree/zupapa-bumper-car-v1/joystick-balls) (either with or without heat set inserts)
    * set of [frame parts](https://github.com/gobabygocarswithjoysticks/index/tree/zupapa-bumper-car-v1/frame)
    * two sets of [PVC tees](https://github.com/gobabygocarswithjoysticks/index/tree/zupapa-bumper-car-v1/pvc-tee)
* 10 feet of 3/4 inch PVC pipe
    * 2x 19 in
    * 2x 2.5 in
    * 2x 10.5 in
    * 2x 16 in
    * 1x 7.25 in
    * 1x 16.25 in
    * 2x 9.5 in
* 6 3/4" pvc elbows
* 2 3/4" pvc tees 
* 2x 4-40 nut
* 2x 4-40 1.25 inch machine screw with phillips head
* 12” of 1/4 split loom plastic wire protector tube
* [18x m2.2x14mm screws](https://www.mcmaster.com/95893A174/)
* 2x 1/4-20 nut
* 2x 1/4-20 3/4 inch hex-head bolt
* gap-filling epoxy that's good for plastic
* (optional) PVC cement, alternatively just use the epoxy
* an assembled [joystickpcb](https://github.com/gobabygocarswithjoysticks/gbg-pcb/tree/main/joystickpcb) (I'll include these with any GBG-PCBs that I give out)
* an assembled GBG-PCB

{% include how-to-get-boards.md %}

# Tools needed
* wire strippers
* wire cutters
* small (3mm) flathead screwdriver
* large (6mm) flathead screwdriver
* small (2.0) Phillips screwdriver
* micro USB cable
* pvc pipe cutter
* epoxy
* ductape
* t6 torx screwdriver
* hotglue

Note: these instructions were originally written for the V1 GBG-PCB but it's even easier with the V2 GBG-PCB.

## circuit diagram for V1 GBG-PCB

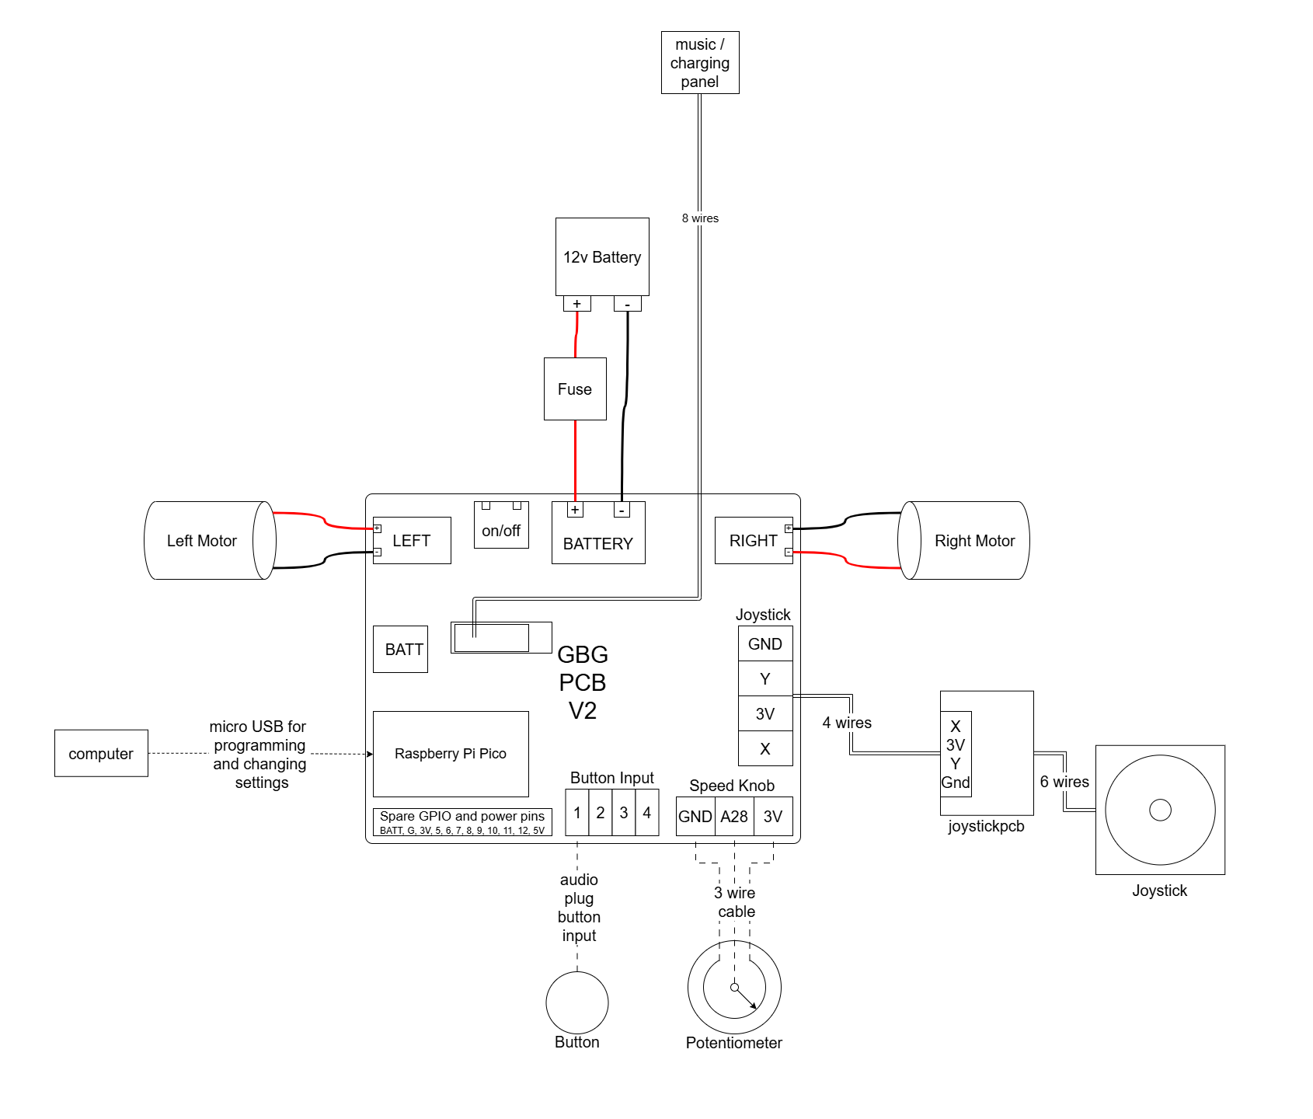
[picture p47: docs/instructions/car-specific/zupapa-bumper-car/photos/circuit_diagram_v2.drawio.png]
circuit diagram for V2 GBG-PCB
## 

## [PCB Schematic](https://github.com/gobabygocarswithjoysticks/gbg-pcb/blob/main/schematic.pdf)
## [PCB List Of Components](https://github.com/gobabygocarswithjoysticks/gbg-pcb/blob/main/PCB_production/BOM.csv)

# Instructions:

# Unpack the Car
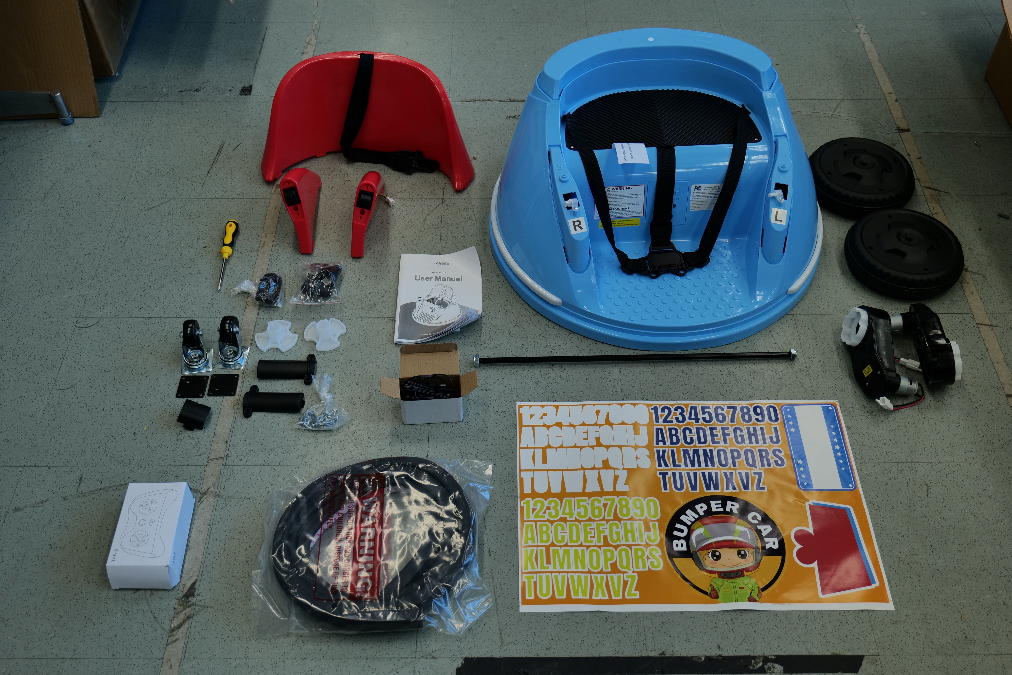
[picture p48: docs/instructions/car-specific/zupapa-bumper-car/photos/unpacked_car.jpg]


# Connect Wheels

The following steps are assembly steps 1 and 2 in the Zupapa bumper car user manual "Install Car Wheels" and "Install Caster Wheels"

## Assemble the axis (Zupapa calls the axel the "axis")
[video instructions](https://www.youtube.com/watch?v=1W5rl3IwcJM)

### On both ends of the axis add a motor, wheel, washer and nut.

Use the included wrenches to tighten the nuts. They are unusual-looking wrenches. Alternatively, if you have normal wrenches you could use them.



Make sure both nuts are fully screwed on until the axis sticks out through them by a millimeter on both ends.

axel_assembly

## Attach the wheels
[video instructions](https://www.youtube.com/watch?v=ZMBXotuPM0Q)

### Turn the car upside down

### Place the axis and wheel assembly into the bottom of the car.

### Plug the two motors into the plugs

### Attach the 2 plastic motor covers with 2 small-head screws each

#### Attach the 2 metal axis covers with 4 small-head screws each

#### Attach the 2 universal (AKA swivel or caster) wheels with 4 large-head screws each

# Electrical Modifications with GBG-PCB with "weelye mode" connectors
## Note: If you have a V2 GBG-PCB, you can modify the zupapa bumper car without cutting any wires

The right motor port should be J105 (TE AMP 1-1123723-2).

Unplug the two motors, the battery, and the 9 wire plug from the control box. Remove the control box.

Plug the motors, battery, and 9 wire plug into the GBG-PCB.

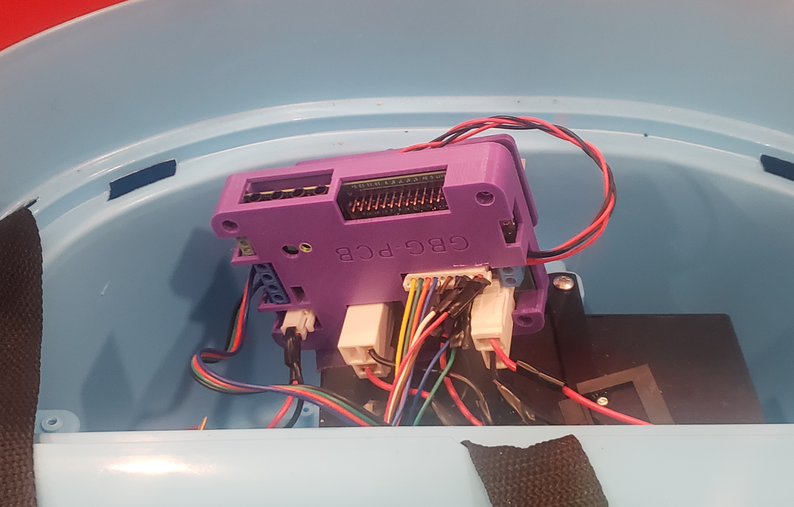
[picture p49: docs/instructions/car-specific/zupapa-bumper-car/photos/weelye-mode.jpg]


Make sure the orientation of the 9 wire plug matches the photo.

Skip ahead in these instructions to wiring the joystick.

# Electrical Modifications with GBG-PCB with screw terminals
[video instructions](https://www.youtube.com/watch?v=aNX1qpSBgc4)

Turn the car back upright
## Remove the Seat and the Battery Cover

Unscrew the 2 screws holding the seat in place and lift it off. Then, unscrew the screw on the white wire holder and the 4 screws holding the battery cover in place and remove the cover.

## Disconnect the battery
It should be shipped with the red wire to the battery already disconnected. If a wire is connected to the red terminal of the battery, disconnect it to keep the car off and safe while you work on it.

Put tape over the red terminal of the battery to prevent accidental short circuits.

## Connect the GBG-PCB
### Connect the on/off switch wire
Find the white wire going to the 9 wire plug on the "weelye" control box that comes with the car. Cut the white wire close to the plug.

Strip a quarter inch (6 mm) of insulation off the end of the white wire. 

Connect the white wire to the on/off terminal closer to the left motor port.


### Connect the PCB to the battery wires
_The PCB can be left connected to the battery. It does not need a switch between itself and the battery. The PCB has MOSFETs that stop electricity from flowing when the on/off switch is off. When the PCB is off it draws practically zero current (2 nanoAmps) so it will not make the battery discharge._

_Unlike other instructions, in this car the Weelye control box that comes with the car is left in the circuit. The GBG-PCB is wired in parallel with the control box from the battery. The control box doesn't control the motors but it does handle charging and power the control panel that does music, lights, charging, and the on/off switch._

#### positive battery wire
Cut the red battery wire close (within an inch) to the fuse box. 

Strip 3/8" (10 mm) of insulation off both ends of the now cut red wire. 

Twist the ends of the red wire back together. 

Connect the wires to the positive large BATTERY screw terminal on the GBG-PCB (labeled "+"). 

Tighten the screw terminal tightly to hold the wires in place.



#### negative battery wire
Cut the black wire so that both ends reach the GBG-PCB. To do that, cut the wire 5 inches (12.7 cm) from the battery. 

Strip 3/8" (10 mm) of insulation off the ends of the now cut black wires. 

Twist the ends of the black wire back together. 

You can unplug the battery plug from the car's control box to make it easier to work.

Connect the wires to the negative large BATTERY screw terminal on the GBG-PCB (labeled "-").

Tighten the screw terminal tightly to hold the wires in place.

Cut the thin black wire off the 6 wire plug. Strip 3/8" (10 mm) of insulation off the end of the black wire.

Put both the black battery wire and the thin black wire from the 6 wire plug into the negative large BATTERY screw terminal on the GBG-PCB (labeled "-"). Tighten the screw terminal securely to hold both wires in place.



### Wire the PCB to the motors
#### left motor
Unplug the left motor from the control box and cut the plug off the ends of the wires. Discard the plug.

Strip 3/8" (10 mm) of insulation off the ends of the two left motor wires. 

Connect the red wire from the left motor to the left motor terminal labeled "+" (the terminal closer to the edge of the board). 

Connect the black wire from the left motor to the left motor terminal labeled "-" (the terminal farther from the edge of the board).



#### right motor
Unplug the right motor from the control box and cut the plug off the ends of the wires. Discard the plug.

Strip 3/8" (10 mm) of insulation off the ends of the two right motor wires.

Connect the red wire from the right motor to the right motor terminal labeled "-" (the terminal farther from the edge of the board). This is reversed from the left motor

Connect the black wire from the right motor to the right motor terminal labeled "+" (the terminal closer to the edge of the board).



If you disconnected the battery plug from the control box, plug it back in.

Place the GBG-PCB into the space behind the control box and the battery



# Wire the joystick
[video instructions](https://www.youtube.com/watch?v=ldmA2Xm-xtc)

Get a 3 foot (1 meter) length of 4 wire cable.

Strip 1/4" (6mm) of insulation from the 4 wires on one end of the cable.

Connect the 4 wires to the screw terminal on the GBG-PCB labeled "joystick." The standard coloring is X=blue, 3V=red, Y=green, gnd=black.

Pry the "control panel" with the charging port, music controls and red on/off switch out of the car.

Reaching through the hole where the control panel was, thread the four wire cable from the GBG-PCB up through the hole in the left armrest of the car.



### Unless a kid, their family, and their doctors all agree that lights and music are ok, removing these distractions are recommended.
The lights can be turned off with a button on the control panel, but they turn on each time the car is turned on. The volume of the music can be changed and the music can be paused (and the car can even be a bluetooth speaker for custom music), but if the speaker is connected the car will play engine noises and then music when it is first turned on.

Unplug the two 4 wire cables from the top of the control panel to turn off the lights. The two plugs that need to be unplugged are circled in the photo.



Reach into the hole where the control panel was and find the plug connecting two yellow wires together. Unplug the yellow wires to turn off the audio.



Push the control panel back into the car.

Strip 1/4" (6mm) of insulation from the 4 wires on the end of the 4 wire cable that is now sticking out of the left armrest

Connect the wires to the screw terminal on the joystick circuit board. Make sure that between the GBG-PCB and the joystick board, the wires are connected in the same order. "X", "3V", "Y", "GND" on the two boards should be connected together. The standard coloring is X=blue, 3V=red, Y=green, gnd=black.



Connect the red battery wire to the battery (it plugs into the tab on the battery then locks into place).



## (optional) Wire Buttons and/or Speed Knob
### Buttons
Plug up to 4 buttons into the headphone-style jacks on the GBG-PCB.

When you connect the GBG-PCB to your computer to change the settings, click the "show all" button and check the box next to "enable button ctrl". Then, you can set what direction each button should make the car move in.

### Speed Knob
You can add a knob to the car for easily adjusting the maximum speed of the car without needing to reprogram it.

Connect a potentiometer to the 3 screw terminals labeled "speed knob". 

When you connect the GBG-PCB to your computer to change the settings, click the "show all" button and check the box next to "use speed knob".

## Reconnect the battery
The cars are sold with a red wire disconnected from the battery to keep the car from turning on during shipping. This also made it safer to work on the electrical system. Now that you're done with the wiring, you can connect the wire to the battery.

# joystick holder

Plug the joystick into the joystick pcb.

Connect the 4 wire cable to the screw terminal on the joystick pcb. Strip 1/4" (6 mm) of insulation off the ends of the wires and connect them to the screw terminal on the joystick pcb.

Hot glue the joystick pcb inside the 3d printed joystick holder so that it can't move around and jam the joystick. Match the position in the photo below.

Add a ziptie to the end of the wire protector, to keep the wires from being pulled out.

joystick pcb photo

Before closing up the joystick holder, drop a 4-40 nut into the slot for the top hole. This nut will be used to secure the joystick holder to the pvc frame later.

Screw the top of the joystick holder to the bottom of the joystick holder, using 4 m2.2x14mm screws. If the joystick is incorrectly rotated, the 3d printed parts won't fit together. The ziptie and wire protector should be inside the joystick holder.

At the other end of the 4 wire cable, in the space under the seat, strip 1/4" (6 mm) of insulation off the ends of the wires. Connect the wires to the screw terminal on the GBG-PCB labeled "joystick". Make sure that between the GBG-PCB and the joystick pcb, the wires are connected in the same order. "X", "3V", "Y", "GN

Cut a 0.75 inch (19mm) by 1.75 inch (45mm) rectangular piece of 1/16” thick rubber gasket sheet.

Put the piece of rubber into the recessed rectangle of the joystick holder clamp. (You may have to trim the piece of rubber to size)

Remove the 4-40 machine screws that are temporarily holding the 4-40 nuts in the joystick holder, taking care not to let the nuts fall out of their slots. Then slide the bolts through the two holes in the 3d printed clamp piece.

Bolt the joystick holder base to the clamp around the PVC crosspiece. It should take almost no force with the screwdriver – if you feel resistance, check the alignment of the nuts and try again. Tighten both bolts similar distances.

Twist the two silver metal pieces off of the joystick threaded shaft and discard.

Screw one of the 3D printed joystick handles onto the shaft of the joystick. Don’t over tighten since you’re screwing into plastic. It may help to drill out the hole with a 3/32" drill bit. 
_Alternatively, you can use the [handle models](https://github.com/gobabygocarswithjoysticks/index/tree/jeep-v1/joystick-balls) modified to use threaded [heat set inserts](https://www.mcmaster.com/94180A333) to connect the joystick handle to the joystick shaft._

Add some hot glue where the joystick wires enter the dashboard and where the joystick wires enter the joystick holder as additional strain relief.

## joystick handles
Twist the two silver metal pieces off of the joystick threaded shaft and discard.

Screw one of the 3D printed joystick handles onto the shaft of the joystick. Don’t over tighten since you’re screwing into plastic. It may help to drill out the hole with a 3/32" drill bit. 
_Alternatively, you can use the [handle models](https://github.com/gobabygocarswithjoysticks/index/tree/jeep-v1/joystick-balls) modified to use threaded [heat set inserts](https://www.mcmaster.com/94180A333) to connect the joystick handle to the joystick shaft._

# frame, backrest, and seatbelt
Use the 6 3d printed [frame parts](https://github.com/gobabygocarswithjoysticks/index/tree/zupapa-bumper-car-v1/frame) and epoxy to assemble the PVC frame and glue it to the car. Use ductape to hold the parts in place as the glue cures.

Assemble the PVC tees, using 10 m2.2x14mm screws. Screw the PVC tees to the 16.25 inch length of PVC using 4 more screws.

Press fit the 1-4-20 handwheel part to the 1/4-20 bolts used with the PVC tees, and add glue if the handwheel is loose.

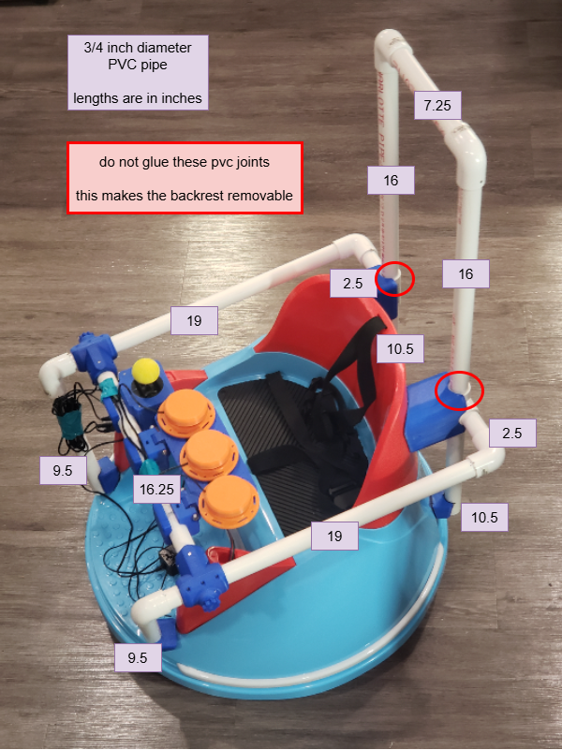
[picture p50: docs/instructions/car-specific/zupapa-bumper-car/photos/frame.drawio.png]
frame photo


# Software and Settings
## Flash the firmware to the Pico
If you got your GBG-PCB from someone who already programmed it for you, then you can skip ahead to Connecting to the car

Go to [the go baby go programmer website](https://gobabygocarswithjoysticks.github.io/programmer/#new) and follow the instructions to upload code to a new car. Select the __PCB_gbg_program__ not the standard __gbg_program__.

## Connecting to the car
### Connect the GBG-PCB to your computer with a micro USB cable
[video of connecting the usb cable](https://www.youtube.com/watch?v=VGhAat-I-ZU)
### Go to [the go baby go programmer website](https://gobabygocarswithjoysticks.github.io/programmer/#configure)
### Follow the instructions pointed to with the magenta arrow to connect to the car
## Calibrate the joystick and adjust settings
### Click the "calibrate the joystick the easy way" button and follow the instructions on the screen
### You can also adjust the speed and acceleration settings for the car.

# Test the car
## disconnect the car from the computer
## turn on the car using the on/off button on the dashboard
### the green light on the PCB should turn on
### you should hear a short beep from the motors
## the car should drive when you move the joystick
### the blue light on the PCB should turn on when the car is moving and turn off when the joystick is centered
### if the blue light blinks quickly that means the joystick needs to be left centered for a few seconds before trying to move and that the joystick may need to be recalibrated

# last steps

Print a [user guide](https://docs.google.com/document/d/10I0WAZf26_EgpSQExoYwdUHBtOAWdVRijO5ywS0Kt0E/edit?usp=sharing) for the car.

Label the "on/off" button (the red switch on the control panel)

### Congratulations! You're done!

# Check your work
Check your work with this [inspection checklist](https://docs.google.com/document/d/1acum34R3Y5wpNdsrZb1wGhzvqPhuyKvQ18ep_NvletY/edit?usp=sharing)

# Troubleshooting

## If you would like help troubleshooting your car or if you have any questions, please email gobabygocarswithjoysticks@gmail.com

# The car doesn't drive in the direction the joystick is pointing in
#### follow these steps to reprogram the car if it drives in the wrong direction:
### 0. Connect the programmer website and calibrate the joystick
### 1. If moving the joystick forwards makes the car spin, use the website to reverse the motor that the car turned towards (show all the settings then press the reverse motor button next to the "motor fast" setting)
### 2. If moving the joystick forwards makes the car drive backwards, use the website to reverse both motors
### 3. If the car spins the opposite direction from the direction that the joystick is points, use the website to swap the motors, then repeat the 3 steps starting at step 1
# The car doesn't drive
## if the blue light blinks quickly
### that means the joystick needs to be left centered for a few seconds before trying to move (this is a safety feature)
#### Let go of the joystick for 5 seconds and wait for the light to stop blinking
### it could also mean that the joystick needs to be recalibrated
#### If the blue light continues to blink quickly after letting go of the joystick for 5 seconds, then you should recalibrate the joystick using the programmer website. Connect the GBG-PCB to your computer, go to the programmer website, connect the website to the GBG-PCB, then click the "calibrate the joystick the easy way" button and follow the instructions on the screen.
## if none of the green lights on the PCB turn on,
#### the battery might have been connected backwards. A backwards connection does not damage the board; the board just doesn't turn on.
#### the on/off switch might not be wired correctly
#### the battery might need to be charged

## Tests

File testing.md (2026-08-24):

V2 boards can supply 8 amps per motor continuously.

With fans running, a V2 GBG-PCB has been tested to supply 11 amps

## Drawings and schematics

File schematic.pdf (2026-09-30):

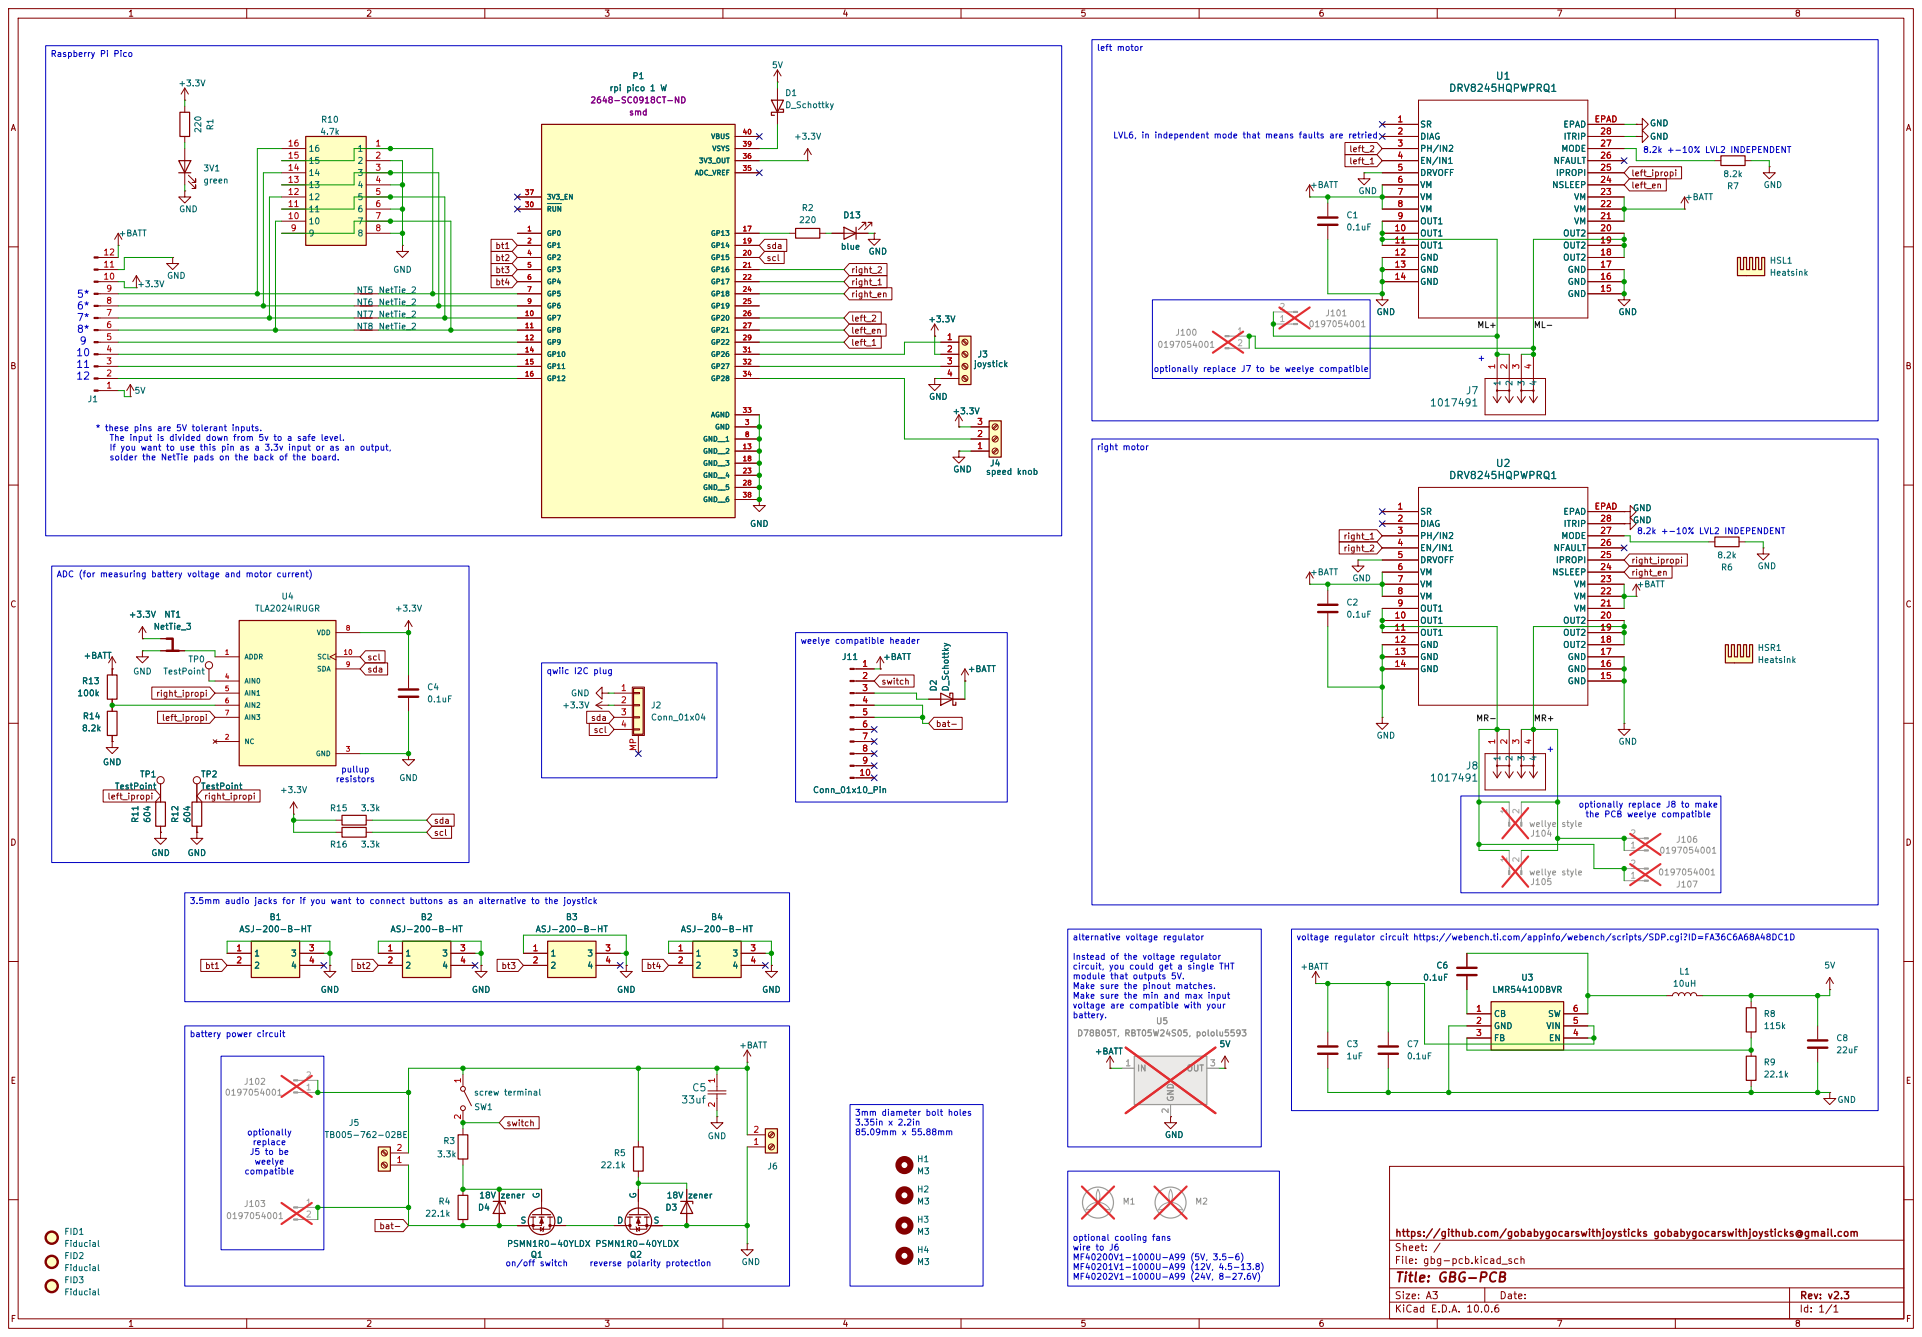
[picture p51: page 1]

LVL6, in independent mode that means faults are retried

optionally replace J7 to be weelye compatible

* these pins are 5V tolerant inputs.
The input is divided down from 5v to a safe level.
If you want to use this pin as a 3.3v input or as an output, solder the NetTie pads on the back of the board.

right motor qwiic I2C plug 3.5mm audio jacks for if you want to connect buttons as an alternative to the joystick

ADC (for measuring battery voltage and motor current)
GND +3.3V

optionally replace J8 to make
the PCB weelye compatible

optional cooling fans wire to J6 MF40200V1-1000U-A99 (5V, 3.5-6) MF40201V1-1000U-A99 (12V, 4.5-13.8) MF40202V1-1000U-A99 (24V, 8-27.6V) alternative voltage regulator

voltage regulator circuit https://webench.ti.com/appinfo/webench/scripts/SDP.cgi?ID=FA36C6A68A48DC1D

Instead of the voltage regulator
circuit, you could get a single THT module that outputs 5V. Make sure the pinout matches. Make sure the min and max input

voltage are compatible with your battery. 3mm diameter bolt holes 3.35in x 2.2in 85.09mm x 55.88mm

https://github.com/gobabygocarswithjoysticks gobabygocarswithjoysticks@gmail.com
Sheet: /
File: gbg-pcb.kicad_sch
Title: GBG-PCB

Size: A3 | Rev: v2.3 | F Date:
KiCad E.D.A. 10.0.6 | Id: 1/1

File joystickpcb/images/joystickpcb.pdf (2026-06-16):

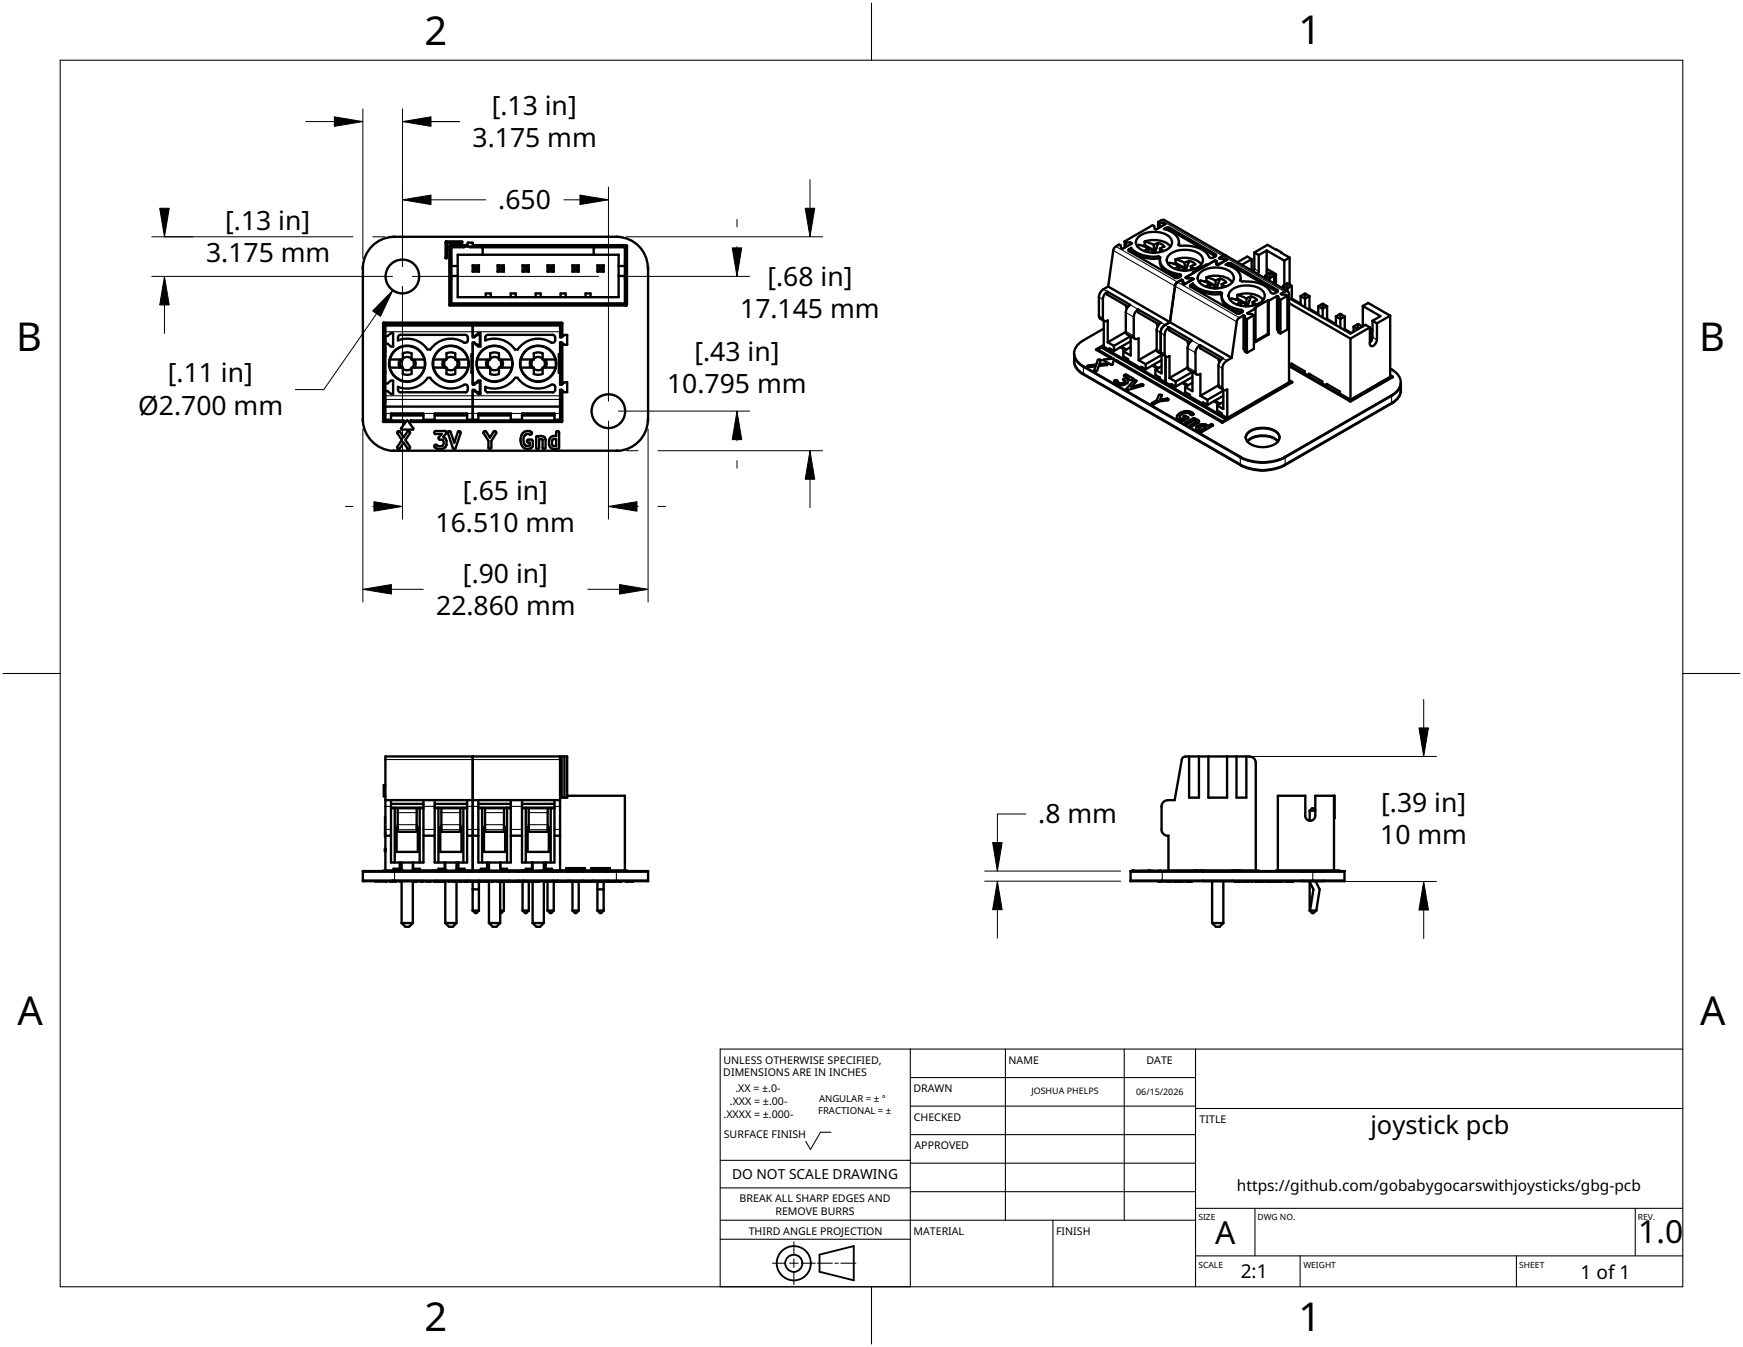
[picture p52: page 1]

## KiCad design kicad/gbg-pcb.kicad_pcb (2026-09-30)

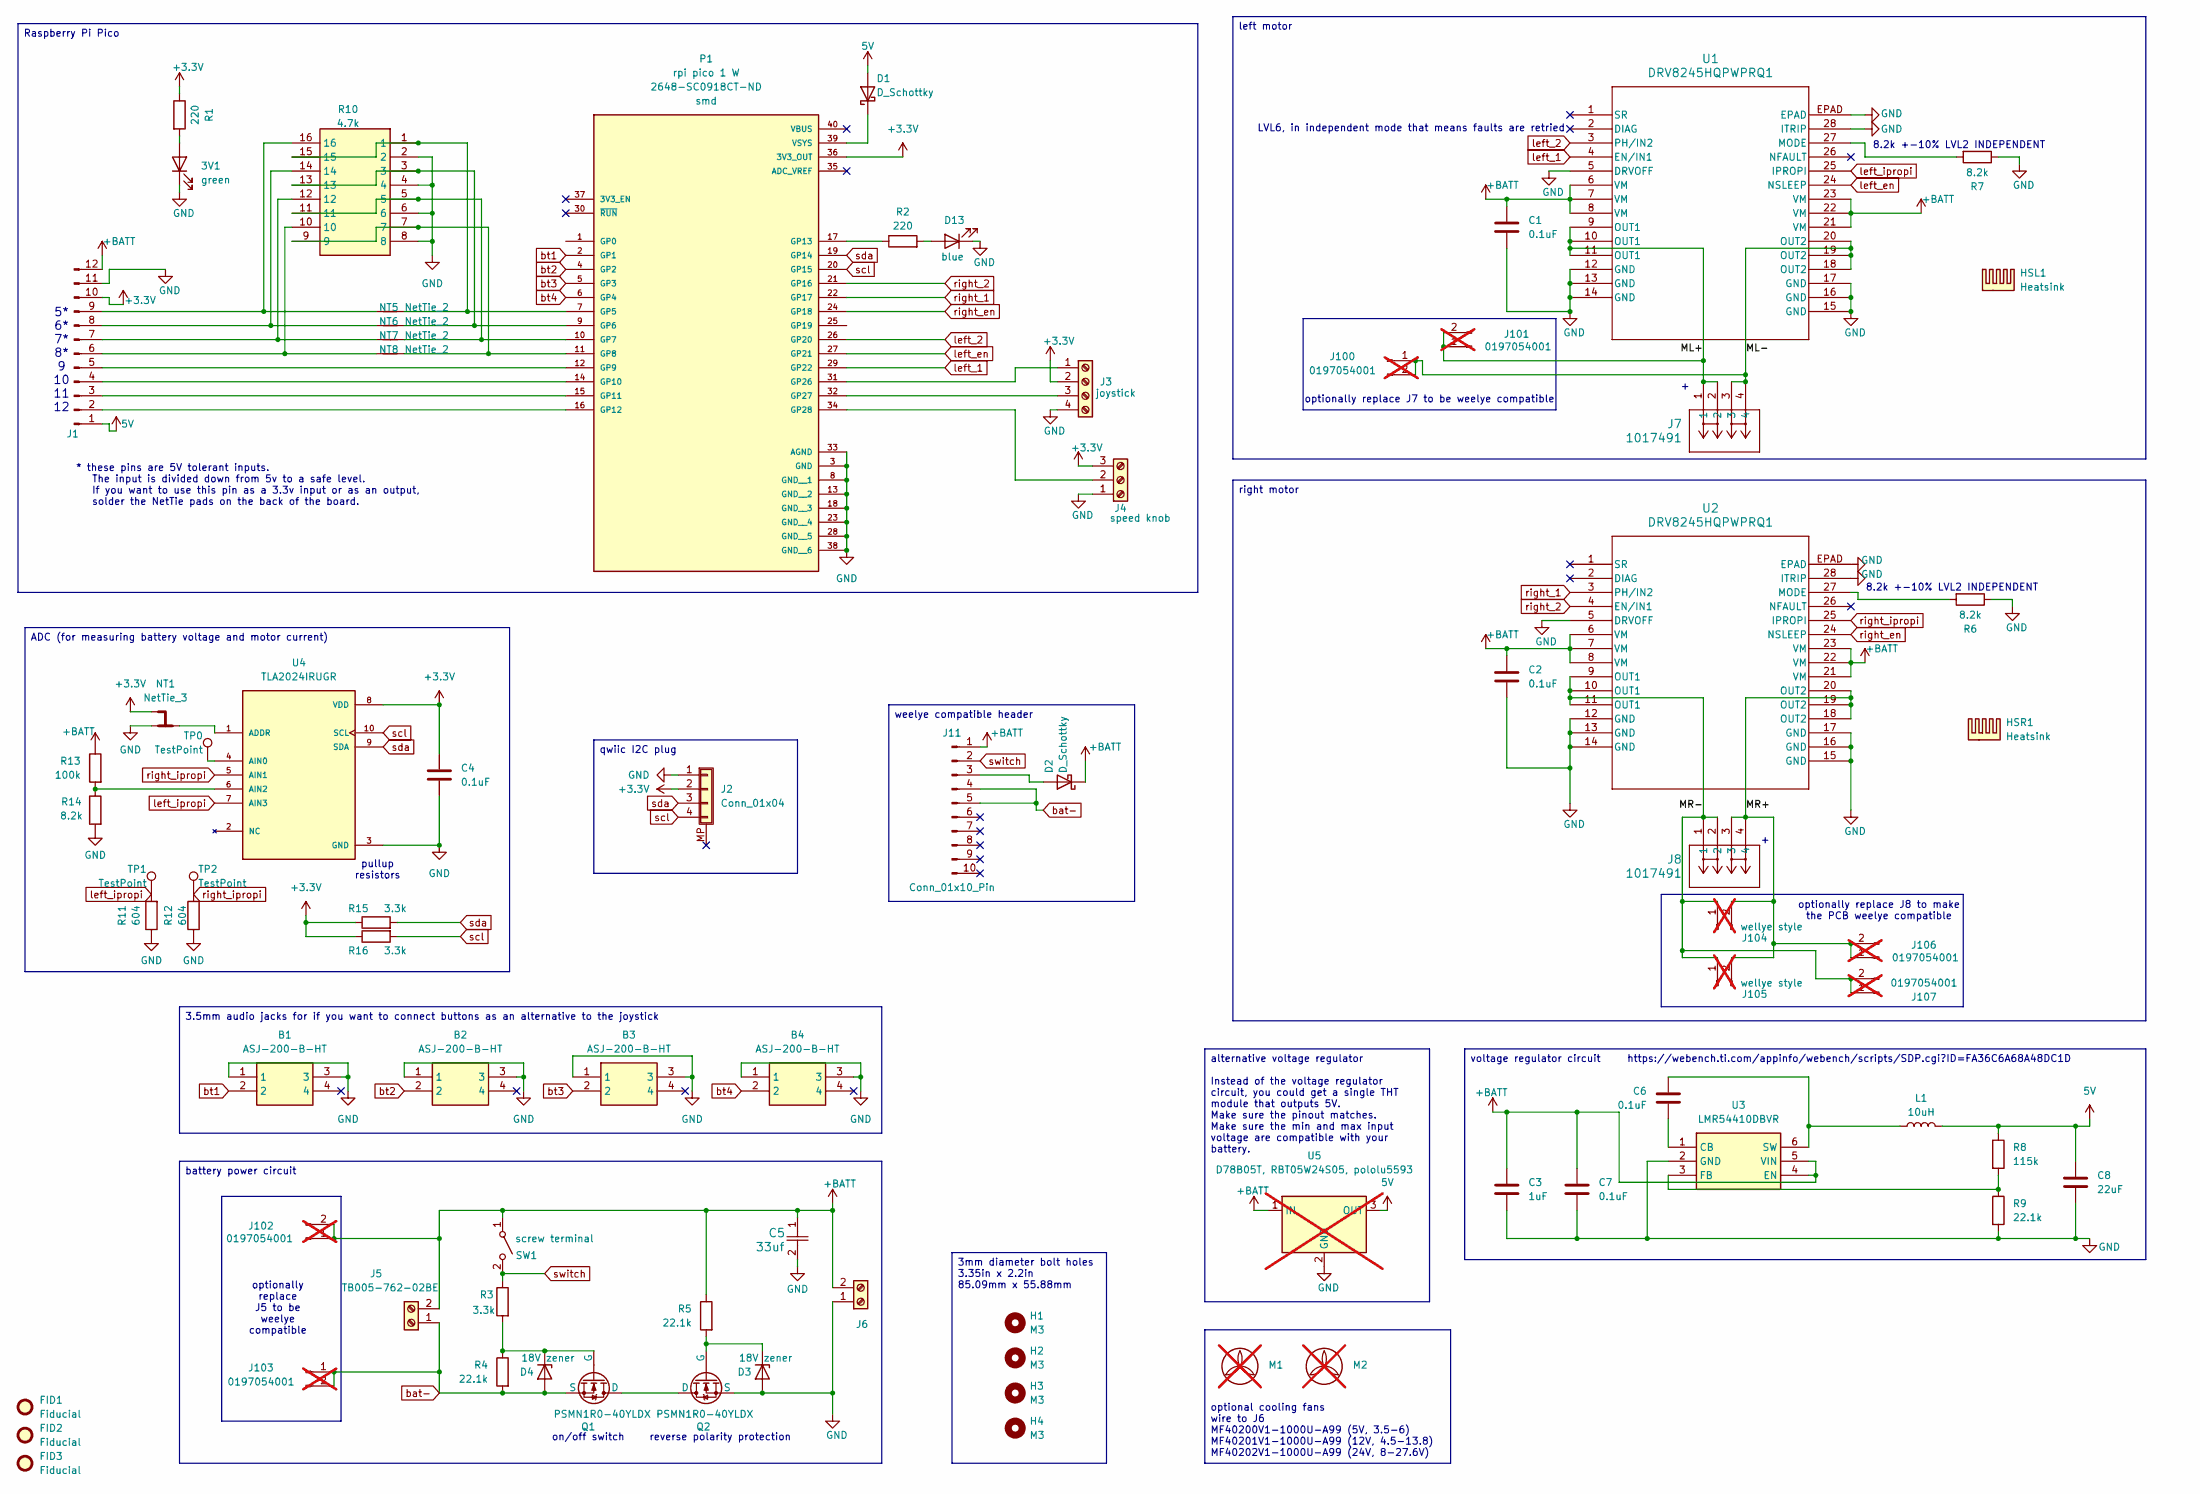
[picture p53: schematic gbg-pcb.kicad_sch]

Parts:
3V1: green; LED_D3.0mm; Manufacturer_Part_Number BL-B2141K; digikey_part_number 2007-BL-B2141K-ND
B1, B2, B3, B4: ASJ-200-B-HT; ASJ200BHT; Manufacturer_Part_Number ASJ-200-B-HT; Mouser Part Number 737-ASJ-200-B-HT
C1, C2, C4: 0.1uF; C_0603_1608Metric; Manufacturer_Part_Number CGA3E2X7R1H104M080AA; digikey_part_number 445-12561-1-ND
C3: 1uF; C_1206_3216Metric; Manufacturer_Part_Number C3216X7R1H105K160AB; digikey_part_number 445-1423-1-ND
C5: 33uf; CAP_KK-8x8_KEM; Manufacturer_Part_Number A759KK336M1JAAE036; digikey_part_number 399-A759KK336M1JAAE036-ND
C6: 0.1uF; C_0603_1608Metric; Manufacturer_Part_Number CGA3E2X7R1E104K080AA; digikey_part_number 445-5667-1-ND
C7: 0.1uF; C_0603_1608Metric; Manufacturer_Part_Number GRM188R72A104KA35D; digikey_part_number 490-3285-1-ND
C8: 22uF; C_1210_3225Metric; Manufacturer_Part_Number MSASE32MSB7226KPNB25; digikey_part_number 587-MSASE32MSB7226KPNB25CT-ND
D1, D2: D_Schottky; D_SOD-123F; Manufacturer_Part_Number FS26; digikey_part_number 4786-FS26CT-ND
D3, D4: 18V zener; D_SOD-123F; Manufacturer_Part_Number MMSZ5248B-E3-18; digikey_part_number MMSZ5248B-E3-18GICT-ND
D13: blue; LED_D5.0mm; Manufacturer_Part_Number BL-BBX1V4V-2-B02; digikey_part_number 2007-BL-BBX1V4V-2-B02-ND
FID1, FID2, FID3: Fiducial; Fiducial_1mm_Mask3mm
H1, H2, H3, H4: M3; MountingHole_3.2mm_M3_ISO7380; Manufacturer_Part_Number DNP; digikey_part_number DNP
HSL1: Heatsink; heatsink 375424B00034G; Manufacturer_Part_Number 375424B00034G; digikey_part_number 375424B00034G-ND
HSR1: Heatsink; heatsink 375424B00034G; Manufacturer_Part_Number 375424B00034G; digikey_part_number 375424B00034G-ND
J1: 12 2.54mm pitch header pins; PinHeader_1x12_P2.54mm_Vertical; Manufacturer_Part_Number PH1-12-UA; digikey_part_number 2057-PH1-12-UA-ND
J2: Conn_01x04; JST_SH_BM04B-SRSS-TB_1x04-1MP_P1.00mm_Vertical; Manufacturer_Part_Number BM04B-SRSS-TB; digikey_part_number 455-BM04B-SRSS-TBCT-ND
J3: joystick; TC0403620000G; Manufacturer_Part_Number TC0403620000G; digikey_part_number TC0403620000G-ND
J4: speed knob; SAMESKY_TB0011-350-03GR; Manufacturer_Part_Number TB0011-350-03GR; digikey_part_number 2223-TB0011-350-03GR-ND
J5: TB005-762-02BE; CUI_TB005-762-02BE; Manufacturer_Part_Number TB005-762-02BE; digikey_part_number 102-6189-ND
J6: screw terminal; EBBA-02-C-SS-BU; Manufacturer_Part_Number EBBA-02-C-SS-BU; digikey_part_number 2057-EBBA-02-C-SS-BU-ND
J7, J8: 1017491; CONN_1017491; Manufacturer_Part_Number 1017491; digikey_part_number 277-17493-ND
J11: Conn_01x10_Pin; PinHeader_1x10_P2.54mm_Vertical; Manufacturer_Part_Number PH1-10-UA; digikey_part_number 2057-PH1-10-UA-ND
J100, J101, J102, J103, J106, J107: 0197054001; Manufacturer_Part_Number 0197054001; digikey_part_number WM2982-ND; not fitted
J104: wellye style; CONN02_2159151002_MOL; Manufacturer_Part_Number 2159151002; digikey_part_number 23-2159151002-ND; not fitted
J105: wellye style; TE_1-1123723-2; Manufacturer_Part_Number 1-1123723-2; digikey_part_number A111830-ND; not fitted
L1: 10uH; IND_SRR6038; Manufacturer_Part_Number SRR6038-100Y; digikey_part_number SRR6038-100YCT-ND
M1, M2: [5V, 3.5-6] MF40200V1-1000U-A99, or [12V, 4.5-13.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; Manufacturer_Part_Number [5V, 3.5-6] MF40200V1-1000U-A99, or [12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; digikey_part_number [5V, 3.5-6] MF40200V1-1000U-A99, or [12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; not fitted
NT1: NetTie_3; SolderJumper-3_P1.3mm_Bridged12_RoundedPad1.0x1.5mm; Manufacturer_Part_Number DNP; digikey_part_number DNP
NT5, NT6, NT7, NT8: NetTie_2; SolderJumper-2_P1.3mm_Open_RoundedPad1.0x1.5mm; Manufacturer_Part_Number DNP; digikey_part_number DNP
P1: rpi pico 1 W; RaspberryPi_Pico_Common_SMD; Manufacturer_Part_Number SC0918; digikey_part_number 2648-SC0918CT-ND
Q1, Q2: PSMN1R0-40YLDX; LFPAK56; Manufacturer_Part_Number PSMN1R0-40YLDX; digikey_part_number 1727-1856-1-ND
R1, R2: 220; R_0805_2012Metric; Manufacturer_Part_Number CRCW0805220RJNEA; digikey_part_number 541-220ACT-ND
R3, R15, R16: 3.3k; R_0805_2012Metric; Manufacturer_Part_Number CRCW08053K30FKEA; digikey_part_number 541-3.30KCCT-ND
R4, R5, R9: 22.1k; R_0805_2012Metric; Manufacturer_Part_Number CRCW080522K1FKEA; digikey_part_number 541-22.1KCCT-ND
R6, R7, R14: 8.2k; R_0805_2012Metric; Manufacturer_Part_Number CRCW08058K20JNEA; digikey_part_number 541-8.2KACT-ND
R8: 115k; R_0805_2012Metric; Manufacturer_Part_Number CRCW0805115KFKEA; digikey_part_number 541-115KCCT-ND
R10: 4.7k; 742C163472JP; Manufacturer_Part_Number 742C163472JP; digikey_part_number 60-742C163472JPCT-ND
R11, R12: 604; R_0805_2012Metric; Manufacturer_Part_Number CRCW0805604RFKEA; digikey_part_number 541-604CCT-ND
R13: 100k; R_0805_2012Metric; Manufacturer_Part_Number CRCW0805100KFKEA; digikey_part_number 541-100KCCT-ND
SW1: screw terminal; EBBA-02-C-SS-BU; Manufacturer_Part_Number EBBA-02-C-SS-BU; digikey_part_number 2057-EBBA-02-C-SS-BU-ND
TP0: TestPoint; TestPoint_THTPad_D2.0mm_Drill1.0mm; Manufacturer_Part_Number DNP; digikey_part_number DNP
TP1, TP2: TestPoint; TestPoint_Pad_D2.0mm; Manufacturer_Part_Number DNP; digikey_part_number DNP
U1, U2: DRV8245HQPWPRQ1; HTSSOP28_PWP_TEX; Manufacturer_Part_Number DRV8245HQPWPRQ1; digikey_part_number 296-DRV8245HQPWPRQ1CT-ND
U3: LMR54410DBVR; SOT95P280X145-6N; Mouser Part Number 595-LMR54410DBVR
U4: TLA2024IRUGR; IC_TLA2024IRUGR; Mfr PN TLA2024IRUGR; digikey_part_number 296-51661-1-ND
U5: D78B05T, RBT05W24S05, pololu5593; D78B05T-1.0; not fitted

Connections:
5V: C8.1, D1.2 (A), J1.1, L1.2, R8.1, U5.3 (OUT)
+3.3V: C4.1, J1.10, J2.2, J3.2, J4.3, NT1.3, P1.36 (3V3_OUT), R1.1, R15.1, R16.1, U4.8 (VDD)
+BATT: C1.1, C2.1, C3.1, C5.1, C7.1, D2.1 (K), J1.12, J5.2, J6.2, J11.1, J102.1, J102.2, R5.1, R13.1, SW1.1 (A), U1.6 (VM), U1.7 (VM), U1.8 (VM), U1.21 (VM), U1.22 (VM), U1.23 (VM), U2.6 (VM), U2.7 (VM), U2.8 (VM), U2.21 (VM), U2.22 (VM), U2.23 (VM), U3.4 (EN), U3.5 (VIN), U5.1 (IN)
/ML+: J7.1, J7.2, J101.1, J101.2, U1.9 (OUT1), U1.10 (OUT1), U1.11 (OUT1)
/ML-: J7.3, J7.4, J100.1, J100.2, U1.18 (OUT2), U1.19 (OUT2), U1.20 (OUT2)
/MR+: J8.3, J8.4, J104.2, J105.2, J106.1, J106.2, U2.18 (OUT2), U2.19 (OUT2), U2.20 (OUT2)
/MR-: J8.1, J8.2, J104.1, J105.1, J107.1, J107.2, U2.9 (OUT1), U2.10 (OUT1), U2.11 (OUT1)
GND: 3V1.1 (K), B1.1, B1.3, B2.1, B2.3, B3.1, B3.3, B4.1, B4.3, C1.2, C2.2, C3.2, C4.2, C5.2, C7.2, C8.2, D3.2 (A), D13.1 (K), J1.11, J2.1, J3.4, J4.1, J6.1, NT1.1, P1.3 (GND), P1.8 (GND__1), P1.13 (GND__2), P1.18 (GND__3), P1.23 (GND__4), P1.28 (GND__5), P1.33 (AGND), P1.38 (GND__6), Q2.1 (S), Q2.2, Q2.3, R6.1, R7.1, R9.2, R10.2, R10.4, R10.6, R10.8, R11.1, R12.1, R14.2, U1.5 (DRVOFF), U1.12 (GND), U1.13 (GND), U1.14 (GND), U1.15 (GND), U1.16 (GND), U1.17 (GND), U1.28 (ITRIP), U1.EPAD, U2.5 (DRVOFF), U2.12 (GND), U2.13 (GND), U2.14 (GND), U2.15 (GND), U2.16 (GND), U2.17 (GND), U2.28 (ITRIP), U2.EPAD, U3.2 (GND), U4.3 (GND), U5.2 (GND); also elsewhere on the board
unnamed: 3V1.2 (A), R1.2
unnamed: D1.1 (K), P1.39 (VSYS)
unnamed: D2.2 (A), J11.3
unnamed: D3.1 (K), Q2.4 (G), R5.2
unnamed: D4.1 (K), Q1.4 (G), R3.2, R4.1
unnamed: D13.2 (A), R2.2
unnamed: J1.2, P1.16 (GP12)
unnamed: J1.3, P1.15 (GP11)
unnamed: J1.4, P1.14 (GP10)
unnamed: J1.5, P1.12 (GP9)
unnamed: J1.6, NT8.1, R10.10
unnamed: J1.7, NT7.1, R10.12
unnamed: J1.8, NT6.1, R10.14
unnamed: J1.9, NT5.1, R10.16
unnamed: J3.1, P1.31 (GP26)
unnamed: J3.3, P1.32 (GP27)
unnamed: J4.2, P1.34 (GP28)
unnamed: NT5.2, P1.7 (GP5), R10.1, R10.15
unnamed: NT6.2, P1.9 (GP6), R10.3, R10.13
unnamed: NT7.2, P1.10 (GP7), R10.5, R10.11
unnamed: NT8.2, P1.11 (GP8), R10.7, R10.9
unnamed: P1.17 (GP13), R2.1
unnamed: Q1.5 (D), Q2.5 (D)
unnamed: R7.2, U1.27 (MODE)
unnamed: R6.2, U2.27 (MODE)
unnamed: C6.2, U3.1 (CB)
unnamed: R8.2, R9.1, U3.3 (FB)
unnamed: C6.1, L1.1, U3.6 (SW)
unnamed: NT1.2, U4.1 (ADDR)
unnamed: TP0.1 (1_1), U4.4 (AIN0)
unnamed: R13.2, R14.1, U4.6 (AIN2)
bat-: D4.2 (A), J5.1, J11.4, J11.5, J103.1, J103.2, Q1.1 (S), Q1.2, Q1.3, R4.2
bt1: B1.2, P1.2 (GP1)
bt2: B2.2, P1.4 (GP2)
bt3: B3.2, P1.5 (GP3)
bt4: B4.2, P1.6 (GP4)
left_1: P1.29 (GP22), U1.4 (EN/IN1)
left_2: P1.26 (GP20), U1.3 (PH/IN2)
left_en: P1.27 (GP21), U1.24 (NSLEEP)
left_ipropi: R11.2, TP1.1 (1_1), U1.25 (IPROPI), U4.7 (AIN3)
right_1: P1.22 (GP17), U2.3 (PH/IN2)
right_2: P1.21 (GP16), U2.4 (EN/IN1)
right_en: P1.24 (GP18), U2.24 (NSLEEP)
right_ipropi: R12.2, TP2.1 (1_1), U2.25 (IPROPI), U4.5 (AIN1)
scl: J2.4, P1.20 (GP15), R16.2, U4.10 (SCL)
sda: J2.3, P1.19 (GP14), R15.2, U4.9 (SDA)
switch: J11.2, R3.1, SW1.2 (B)

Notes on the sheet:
8.2k +-10% LVL2 INDEPENDENT
on/off switch
LVL6, in independent mode that means faults are retried
optionally replace J8 to make the PCB weelye compatible
optionally replace J7 to be weelye compatible
pullup resistors
5* 6* 7* 8* 9 10 11 12
optionally replace J5 to be weelye compatible
reverse polarity protection
* these pins are 5V tolerant inputs. The input is divided down from 5v to a safe level. If you want to use this pin as a 3.3v input or as an output, solder the NetTie pads on the back of the board.
optional cooling fans wire to J6 MF40200V1-1000U-A99 (5V, 3.5-6) MF40201V1-1000U-A99 (12V, 4.5-13.8) MF40202V1-1000U-A99 (24V, 8-27.6V)
3mm diameter bolt holes 3.35in x 2.2in 85.09mm x 55.88mm
right motor
ADC (for measuring battery voltage and motor current)
weelye compatible header
battery power circuit
3.5mm audio jacks for if you want to connect buttons as an alternative to the joystick
alternative voltage regulator Instead of the voltage regulator circuit, you could get a single THT module that outputs 5V. Make sure the pinout matches. Make sure the min and max input voltage are compatible with your battery.
voltage regulator circuit https://webench.ti.com/appinfo/webench/scripts/SDP.cgi?ID=FA36C6A68A48DC1D
qwiic I2C plug
left motor
Raspberry Pi Pico

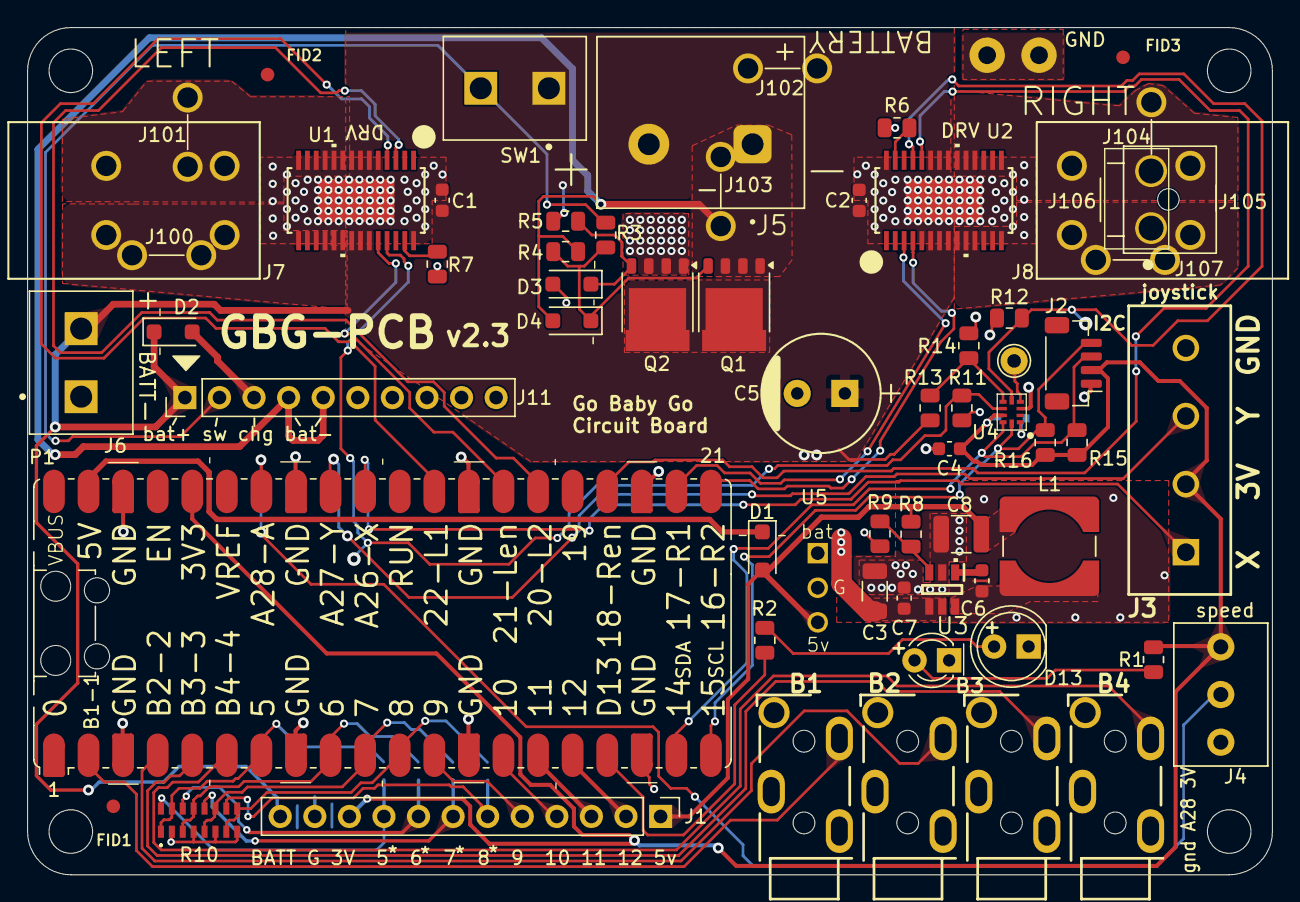
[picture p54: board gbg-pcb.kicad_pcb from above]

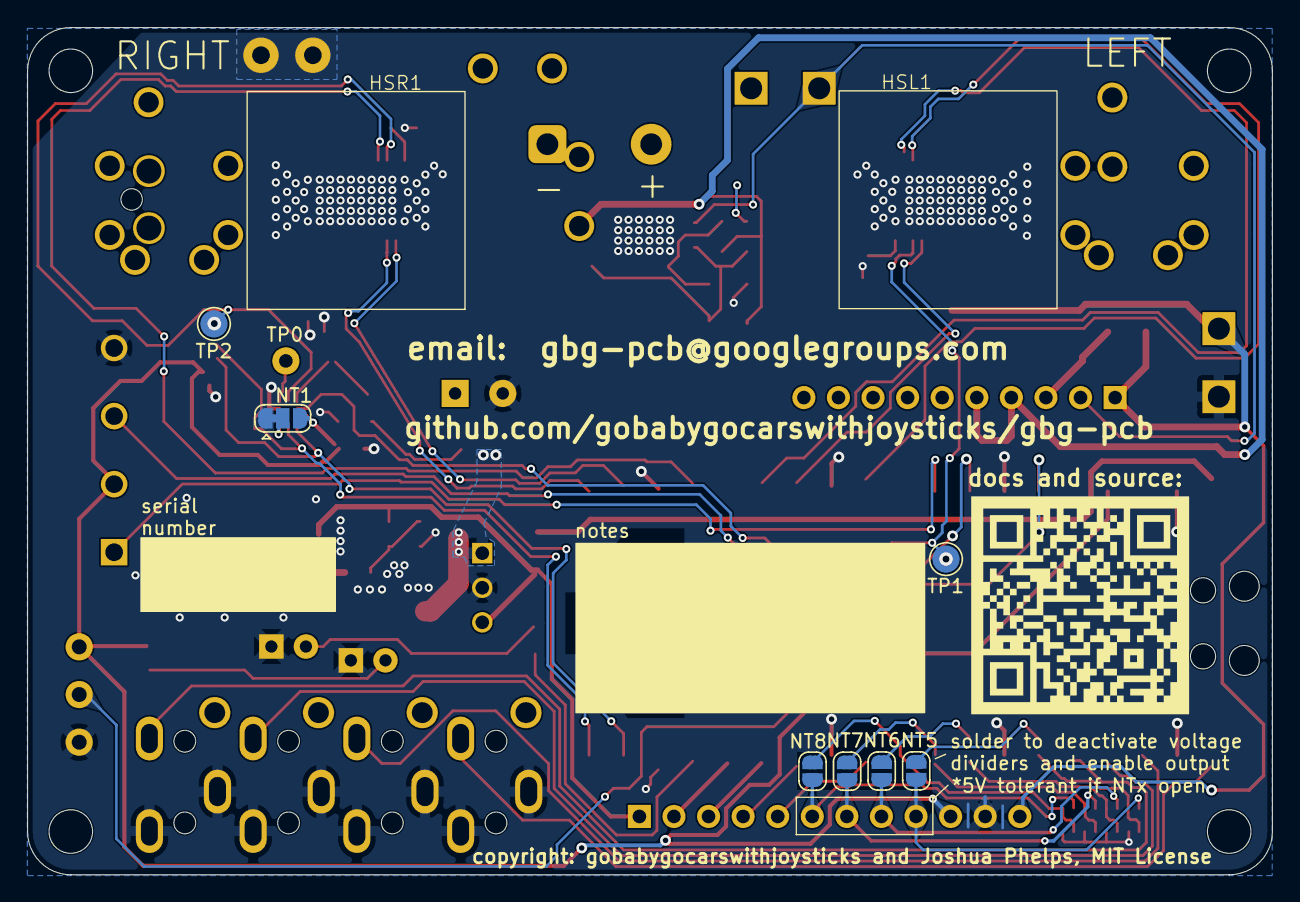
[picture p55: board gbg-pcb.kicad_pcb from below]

Board: 2 copper layers, 91.4 x 62.2 mm, 79 parts (9 on the bottom side), 55 nets.

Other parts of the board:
JGND2: Conn_01x02; TestPoint_Bridge_Pitch3.81mm_Drill1.3mm

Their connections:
GND: JGND2.1 (Pin_1_1); also elsewhere on the board

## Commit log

2025-03-18 starting to redo motor driver circuit
    [gbg-pcb.kicad_pcb, gbg-pcb.kicad_sch]
2025-03-18 BOT process kicad
    [BOM.csv]
2025-03-18 start to change to gate drivers and individual mosfets
    [P78E05-1000.step, gbg-pcb.kicad_pcb, gbg-pcb.kicad_sch]
2025-03-22 start layout
    [D78B05T-1.0.step, gbg-pcb.kicad_pcb]
2025-03-22 work on layout
    [gbg-pcb.kicad_pcb, gbg-pcb.kicad_sch]
2025-03-23 add heatsink
    [gbg-pcb.kicad_pcb, gbg-pcb.kicad_sch, sk_675_100_al.stp]
2025-03-23 place components
    [gbg-pcb.kicad_pcb, gbg-pcb.kicad_sch]
2025-03-23 add traces
    [gbg-pcb.kicad_pcb, gbg-pcb.kicad_sch]
2025-03-23 capacitors and labels
    [gbg-pcb.kicad_pcb, gbg-pcb.kicad_sch]
2025-03-23 tape and silkscreen
    [1mmcube.step, gbg-pcb.kicad_pcb, gbg-pcb.kicad_sch]
2025-04-10 widen left driver's ground
    [gbg-pcb.kicad_pcb]
2026-05-21 pull from gbg-pcb-2
    [1017491.stp, 375424B00034G.stp, 63900-1--3DModel-STEP-1(1).STEP, A759KC276M1JAAE054.step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]
2026-05-21 BOT render images
    [gbg-pcb.step]
2026-05-22 change bat- trace
    [gbg-pcb.kicad_pcb, gbg-pcb.kicad_sch]
2026-05-23 layout final tweak
    [gbg-pcb.kicad_pcb]
2026-05-23 adjust traces
    [gbg-pcb.kicad_pcb]
2026-05-23 adjust silkscreen
    [gbg-pcb.kicad_pcb]
2026-05-23 update voltage divider
    [gbg-pcb.kicad_pcb, gbg-pcb.kicad_sch]
2026-05-23 mark 5VT pins
    [gbg-pcb.kicad_pcb]
2026-05-26 fix solderstencil, change capacitor part number
    [gbg-pcb.kicad_pcb, gbg-pcb.kicad_sch]
2026-05-27 Update README.md with alternate joystick screw terminal
2026-06-01 update how-to-make-boards with stencil jig
    [stencil-jig.scad, stencil-jig.stl]
2026-06-01 update stencil jig
    [stencil-jig.scad, stencil-jig.stl]
2026-06-04 add photos to instructions and change P1 to SMD in BOM
    [gbg-pcb.kicad_pcb, gbg-pcb.kicad_sch]
2026-06-07 add note about current
2026-06-07 test 5v pins
2026-06-07 edit 5v test image
2026-06-07 document alternate J8
    [gbg-pcb.kicad_pcb, gbg-pcb.kicad_sch]
2026-06-10 BOM for new variant
    [BOM-without-motor-battery-button-connectors.csv]
2026-06-15 joystickpcb to kicad 10 and adding drawing
    [joystickpcb.kicad_pcb, joystickpcb.kicad_sch, joystickpcb.step]
2026-06-15 rotate 3d model
    [gbg-pcb.kicad_pcb]
2026-06-20 add case and fans
    [case.FCStd, gbg-pcb-case-bottom.stl, gbg-pcb-case-fan-funnel.stl, gbg-pcb-case-top.stl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]
2026-06-20 update STLs
    [case.FCStd, gbg-pcb-case-bottom.stl, gbg-pcb-case-fan-funnel.stl, gbg-pcb-case-top.stl]
2026-06-25 update case
    [case.FCStd, gbg-pcb-case-bottom.stl, gbg-pcb-case-fan-cover.stl, gbg-pcb-case-fan-funnel.stl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]

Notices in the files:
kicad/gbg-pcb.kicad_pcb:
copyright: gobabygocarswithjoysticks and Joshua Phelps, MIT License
